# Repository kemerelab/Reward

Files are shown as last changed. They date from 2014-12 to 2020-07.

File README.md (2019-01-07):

Open Source Design for Liquid Reward in Rodent Behavioral Mazes
======

These reward wells are meant to be installed at the ends of a track. When the animal's breaks the infra-red beam at the right
location, liquid reward is delivered either via a pump or valve-controlled gravity-feed system when the animal. 

### Manufacturing
Designs are provided to 3D print the reward well. We have had success with Shapeways "White Strong and Flexible", as well as
printing in-house on our Afinia 3D printer. To prepare the food well, feed wires through the structure of the food well and
solder them to a 5 mm IR LED (e.g., [Digikey part 751-1210](https://www.digikey.com/product-detail/en/vishay-semiconductor-opto-division/TSHF5210/751-1210-ND/1681345)) and a 5 mm IR phototransistor 
(e.g., [Digikey part 475-1080](http://www.digikey.com/short/7zhpv2)). These wires are sheathed in a thick heatshrink to protect them from being eaten and then then soldered to the interface board. After testing for functionality, we expoy the LED and phototransistor into place. We additionally install a luer connection (Value Plastics [KTFLL-1](http://www.nordsonmedical.com/technical/part_drawings/KFTLL.pdf)) into the liquid feed hole at the bottom of the well.

We have ordered interface boards to be manufactured by Seeed Studio, using their PCBA service, at a cost of ~$2/unit.

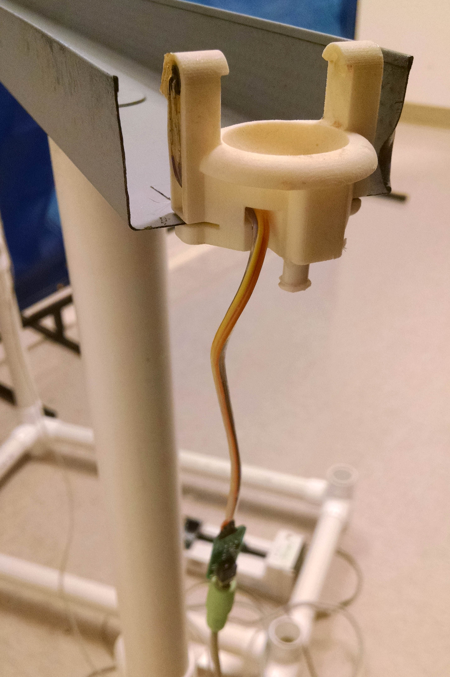
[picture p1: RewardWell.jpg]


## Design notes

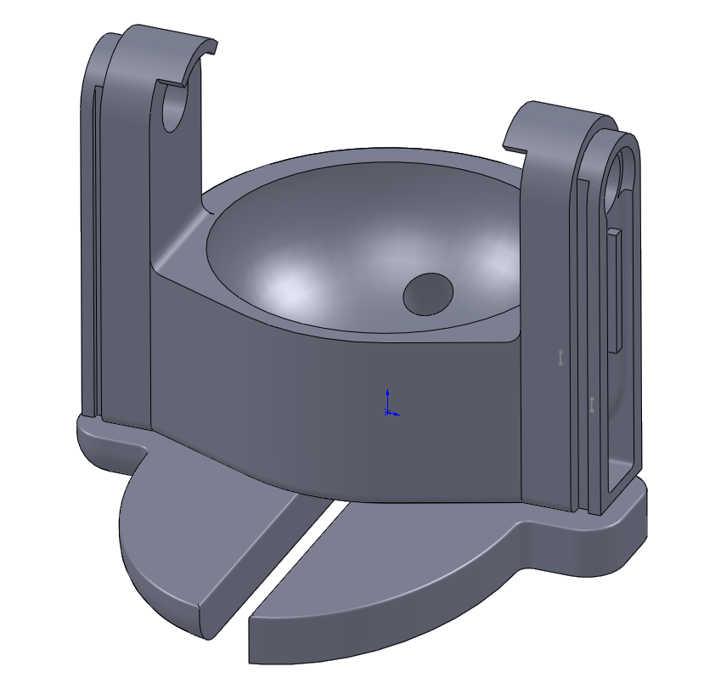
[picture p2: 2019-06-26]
OtherDesigns/RewardWellWithCaps/foodwell-all.png

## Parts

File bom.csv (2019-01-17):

Item | Purpose | Manufacturer | Manufacturer Part # | Distributor | Distributor Part # | Description | Web link
IR LED | Component for beam break system | Vishay Semiconductor | TSHF5210 | Digikey | 751-1210-ND | Emitter IR 890 nm 100 ma radial | https://www.digikey.com/product-detail/en/vishay-semiconductor-opto-division/TSHF5210/751-1210-ND/1681345
IR photodiode | Component for beam break system | Vishay Semiconductor | SFH 313FA | Digikey | 475-1080-ND | Phototransistor NPN 870 nm w/fltr | https://www.digikey.com/short/7zhpv2
Luer Connection | Interface between reward well and tubing | Value Plastics, Inc. |  | Nordson Medical | KFTLL-1 | Female Luer Thread with 1/4” Hex to 10-32 UNF Thread | https://www.nordsonmedical.com/Shop/Fluid-Management/Products/KFTLL-1
4-hole connector | Connection to syringe pump | Molex, LLC. | 3091042 | Digikey | WM1333-ND | Conn Receptacle 4Pos 0.093 | https://www.digikey.com/product-detail/en/molex-llc/0003091042/WM1333-ND/61324
Crimp pins | Pins for 4-hole connector | Molex, LLC. | 02-09-1104 | Digikey | WM1101-ND | Conn Socket 14-20 AWG Crimp Tin | https://www.digikey.com/product-detail/en/molex-llc/02-09-1104/WM1101-ND/26386
Other (don’t need specific part)
3.5 mm stereo audio cables
Arduino

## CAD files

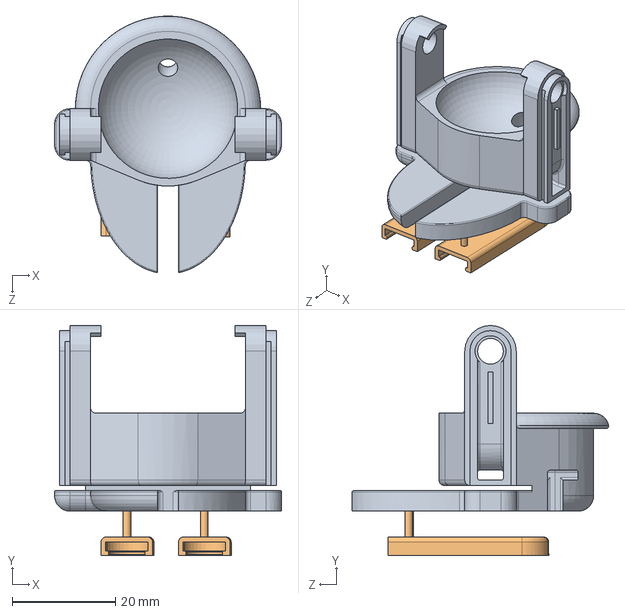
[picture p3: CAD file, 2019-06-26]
OtherDesigns/RewardWellWithCaps/foodwell-with endcaps2.SLDASM
44.0 x 44.6 x 49.7 mm
foodwell_all
foodwell_endcap x 2

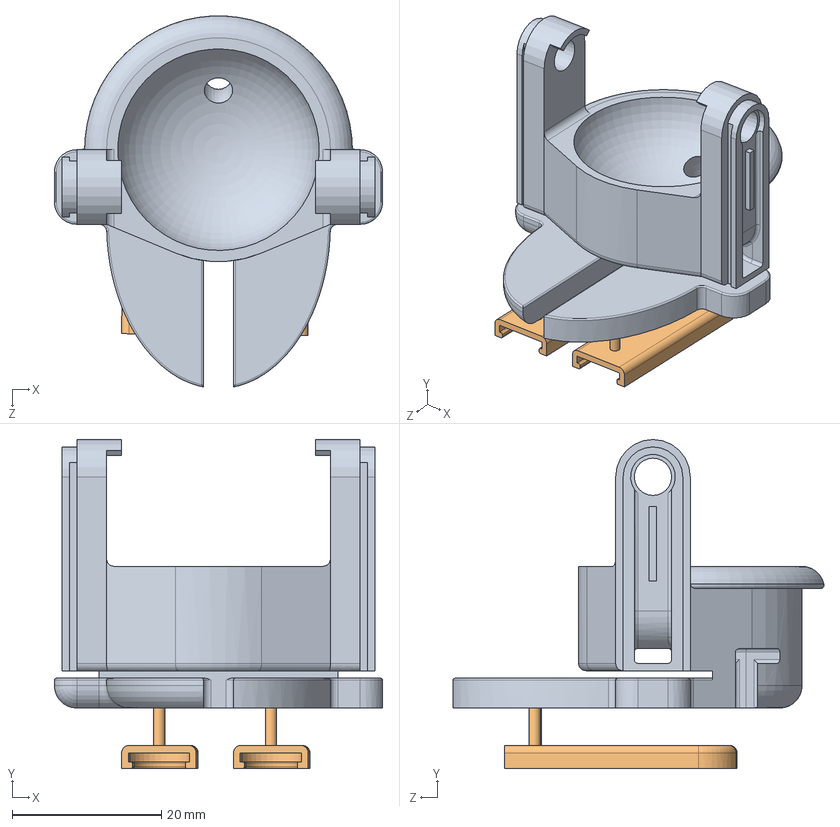
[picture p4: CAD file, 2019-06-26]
OtherDesigns/RewardWellWithCaps/foodwell-with endcaps.SLDASM
44.0 x 44.1 x 49.7 mm
foodwell_all
foodwell_endcap x 2

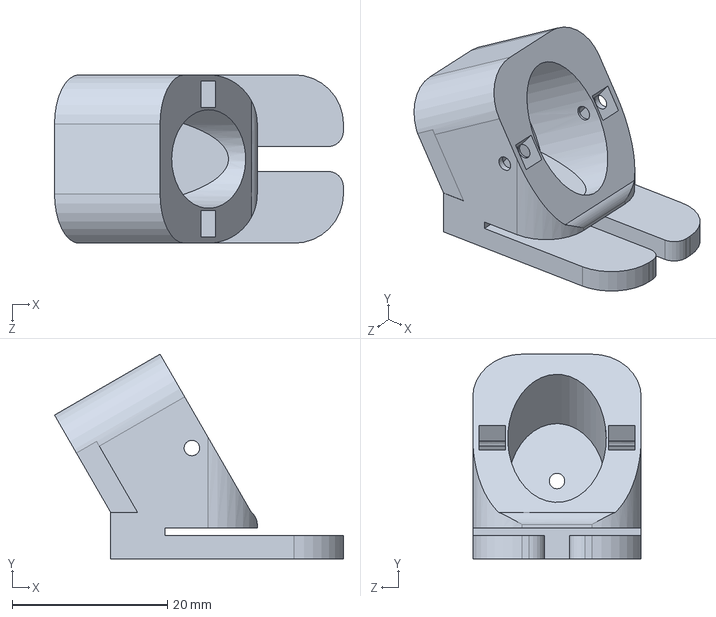
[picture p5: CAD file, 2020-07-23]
OtherDesigns/MouseWithLickSlot v5.SLDPRT
37.2 x 26.4 x 21.7 mm

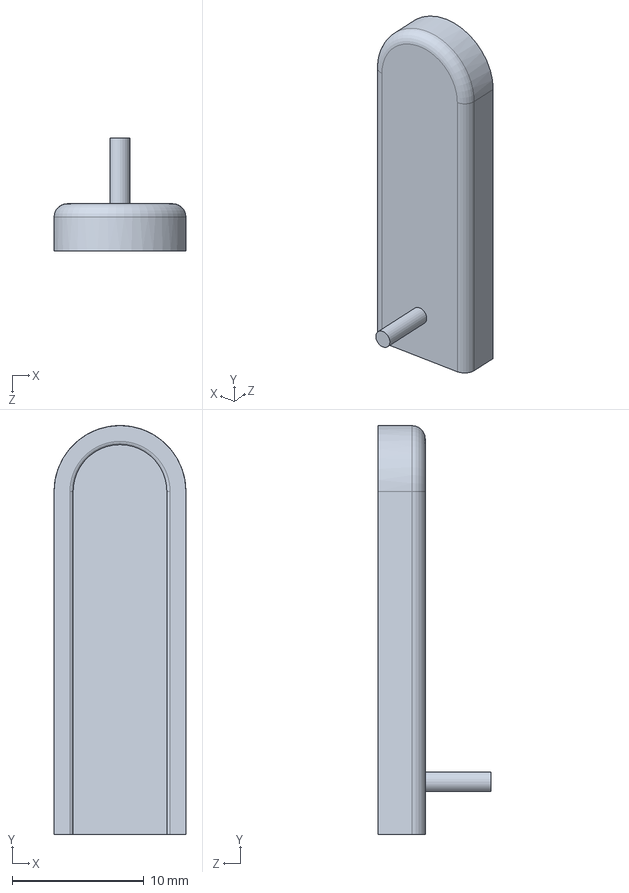
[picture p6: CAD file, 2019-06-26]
OtherDesigns/RewardWellWithCaps/foodwell_endcap.SLDPRT
10.0 x 31.0 x 8.60 mm

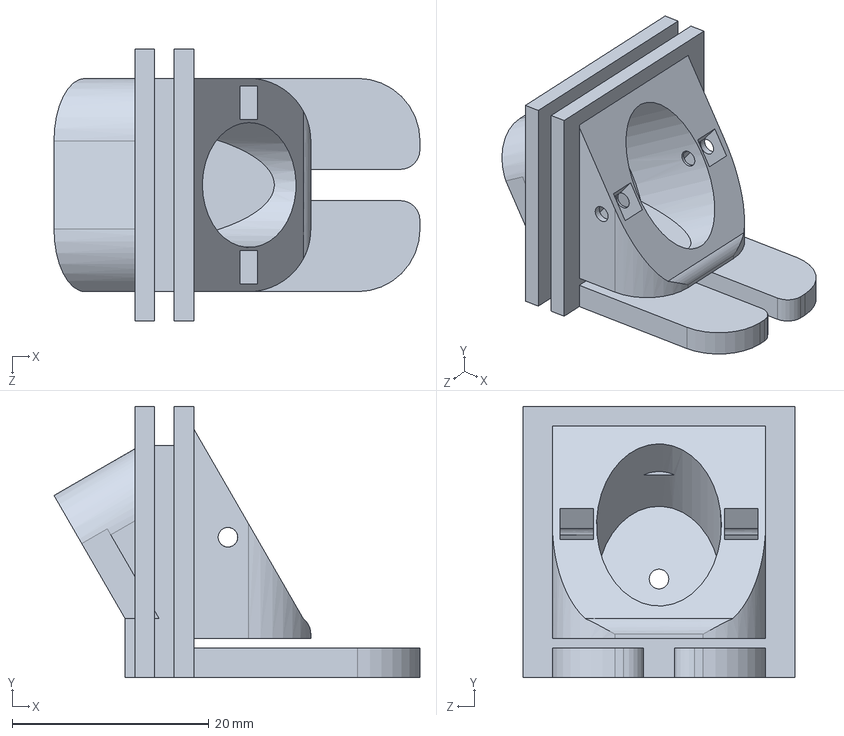
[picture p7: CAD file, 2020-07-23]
OtherDesigns/MouseWithLickSlot v6.SLDPRT
37.2 x 27.6 x 27.7 mm

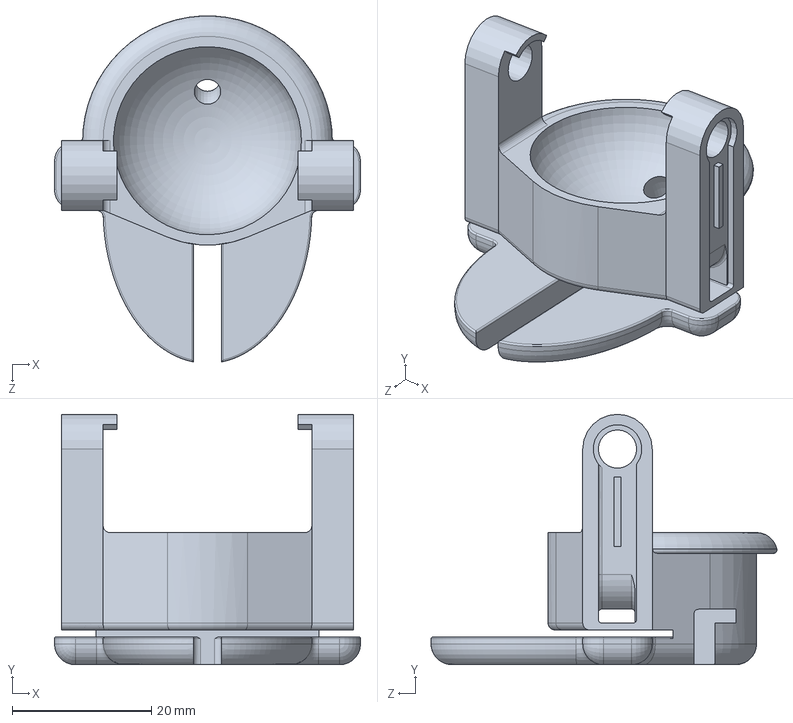
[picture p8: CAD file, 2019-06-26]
OtherDesigns/RewardWellWithCaps/foodwell_nocaps.SLDPRT
44.0 x 36.0 x 49.7 mm

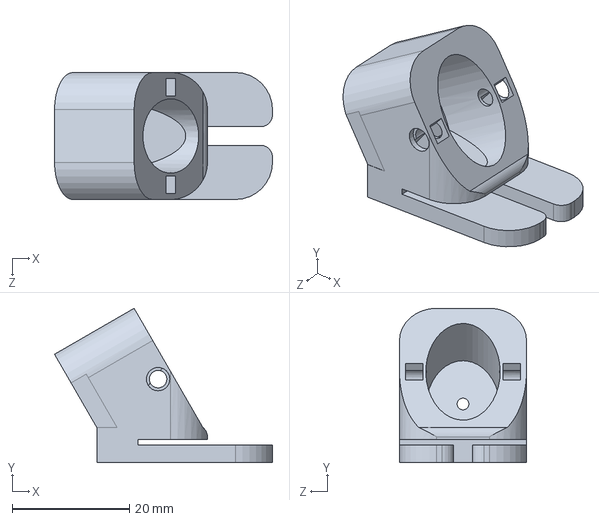
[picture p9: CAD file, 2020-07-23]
OtherDesigns/MouseWithLickSlot v3.SLDPRT
37.2 x 26.4 x 21.7 mm

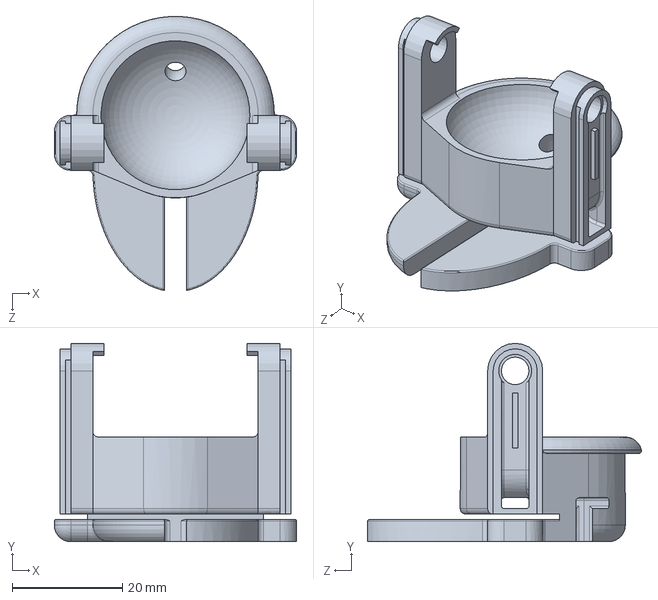
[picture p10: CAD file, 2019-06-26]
OtherDesigns/RewardWellWithCaps/foodwell_all.SLDPRT
44.0 x 36.0 x 49.7 mm

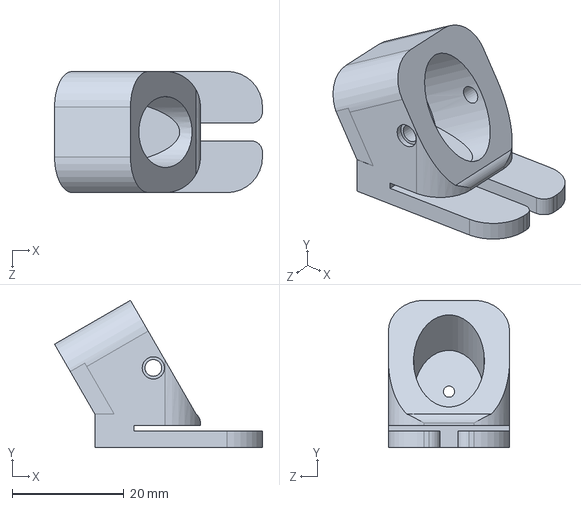
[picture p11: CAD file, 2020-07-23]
OtherDesigns/MouseWithLickSlot v2.SLDPRT
37.2 x 26.4 x 21.7 mm

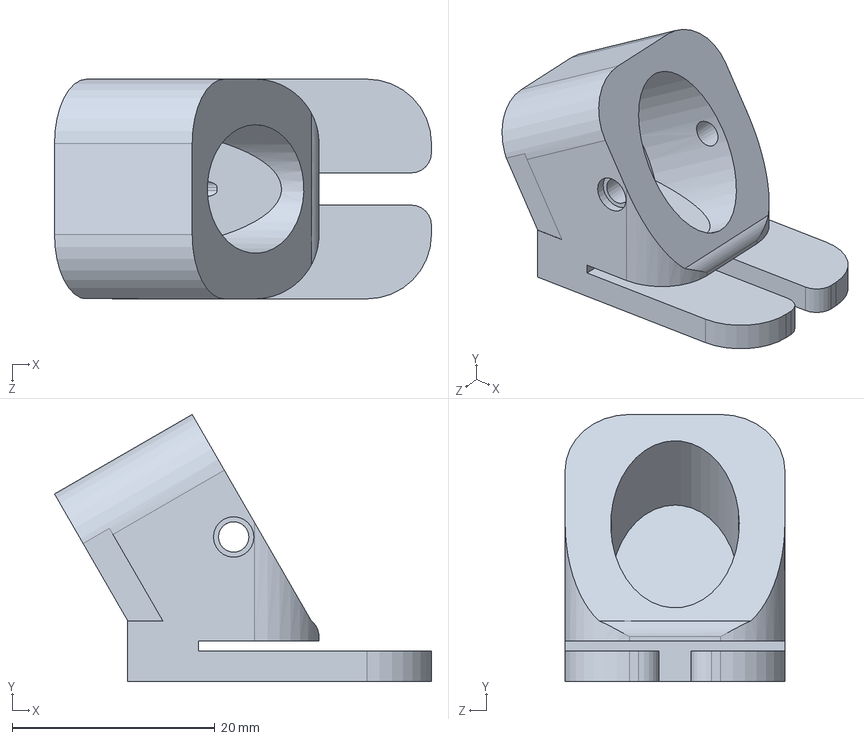
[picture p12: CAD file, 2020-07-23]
OtherDesigns/MouseWithLickSlot.SLDPRT
37.2 x 26.4 x 21.7 mm

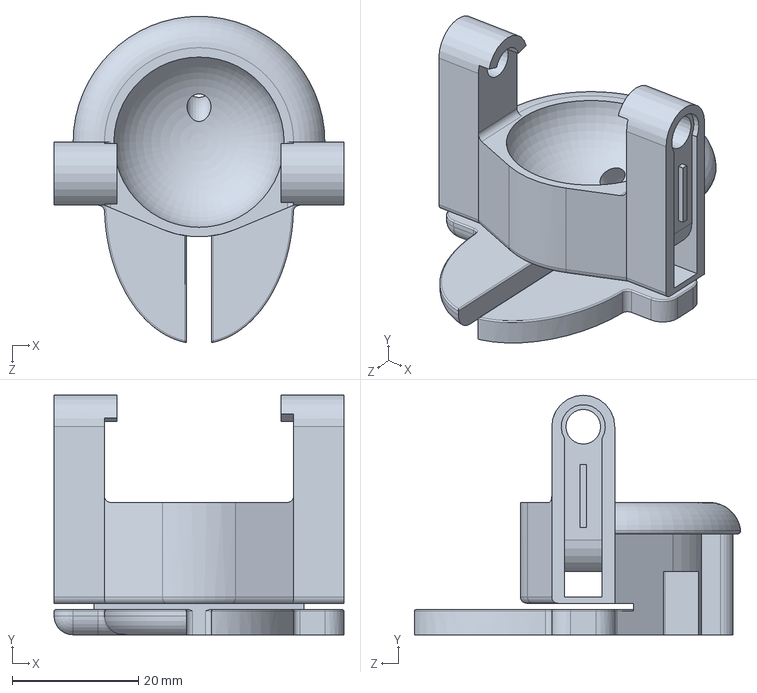
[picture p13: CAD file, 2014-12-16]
OtherDesigns/RewardWellWithCaps/foodwell_nocaps_2.SLDPRT
46.0 x 38.0 x 51.8 mm

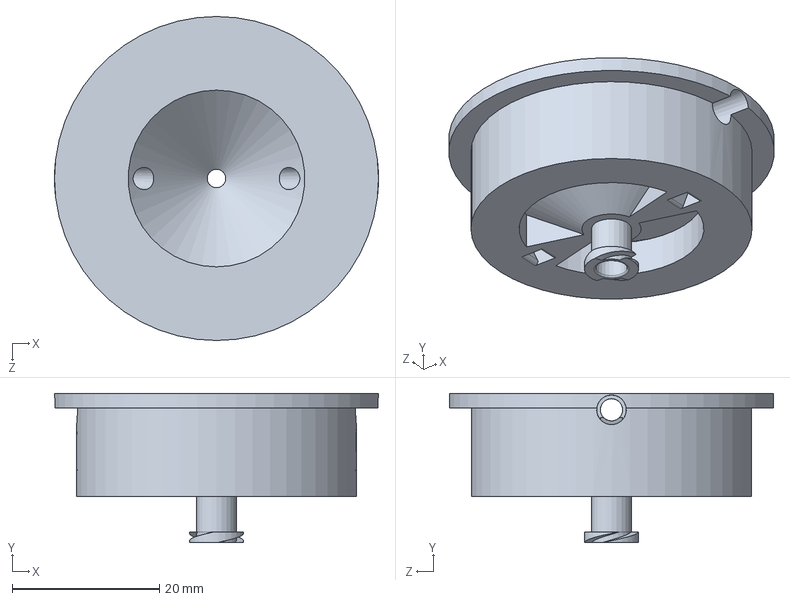
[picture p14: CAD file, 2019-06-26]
OtherDesigns/nosepoke3.SLDPRT
44.0 x 20.3 x 44.0 mm

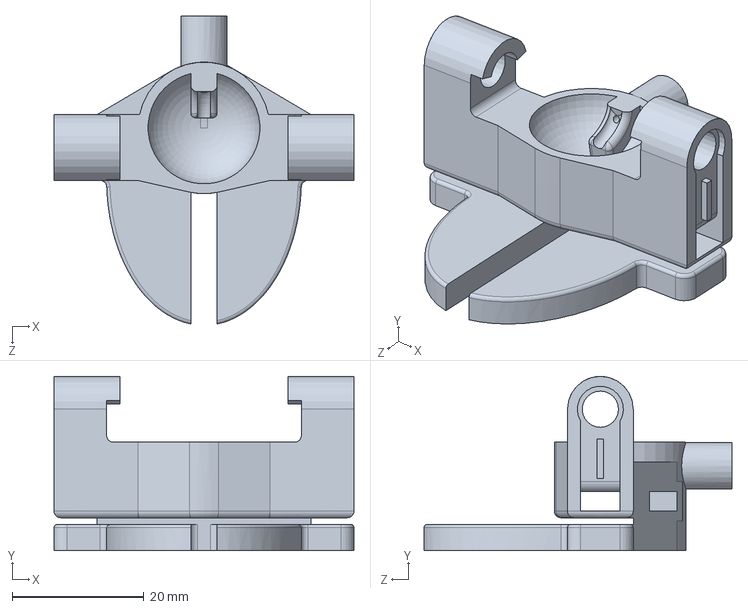
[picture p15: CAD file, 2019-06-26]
OtherDesigns/RewardWellMouse.SLDPRT
45.6 x 26.5 x 46.8 mm

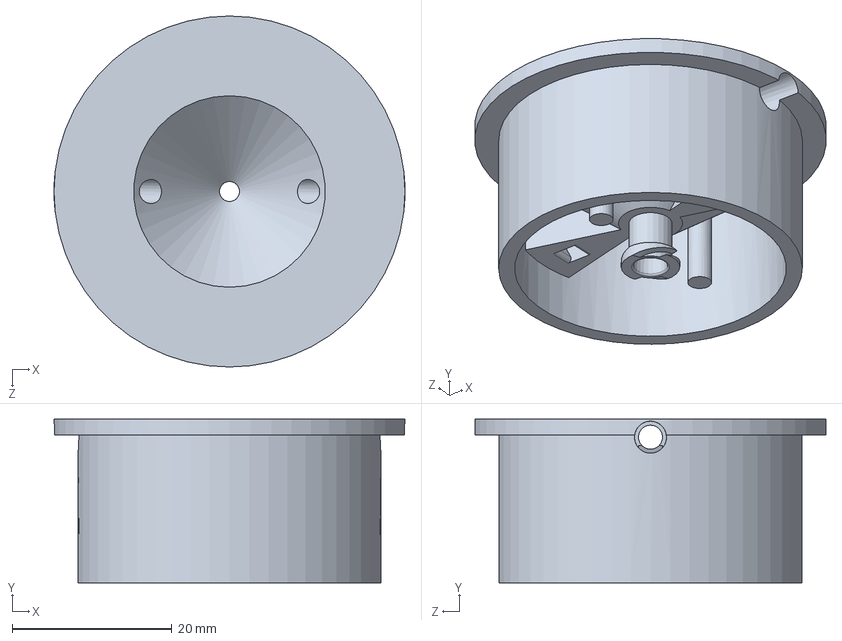
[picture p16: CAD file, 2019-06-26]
OtherDesigns/nosepoke2.SLDPRT
44.0 x 20.5 x 44.0 mm

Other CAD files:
OtherDesigns/MouseWithLickSlot v4.SLDPRT
OtherDesigns/nosepoke.SLDPRT
OtherDesigns/RewardWellMouse2.SLDPRT
OtherDesigns/nosepoke4.SLDPRT
OtherDesigns/MouseWithLickSlot v2.STL
OtherDesigns/MouseWithLickSlot v3.STL
OtherDesigns/MouseWithLickSlot v4.STL
OtherDesigns/MouseWithLickSlot v5.STL
OtherDesigns/MouseWithLickSlot v6.STL
OtherDesigns/MouseWithLickSlot.STL
OtherDesigns/RewardWellMouse3.SLDPRT
OtherDesigns/RewardWellMouse3.STL
OtherDesigns/RewardWellWithCaps/foodwell-with endcaps.STL
OtherDesigns/RewardWellWithCaps/foodwell-with endcaps2.STL
OtherDesigns/RewardWellWithCaps/foodwell_nocaps.STL
OtherDesigns/RewardWellWithCaps/foodwell_nocaps_2.STL
OtherDesigns/foodwell_top.SLDPRT
OtherDesigns/nosepoke2.STL
OtherDesigns/nosepoke3.STL
OtherDesigns/nosepoke4.STL

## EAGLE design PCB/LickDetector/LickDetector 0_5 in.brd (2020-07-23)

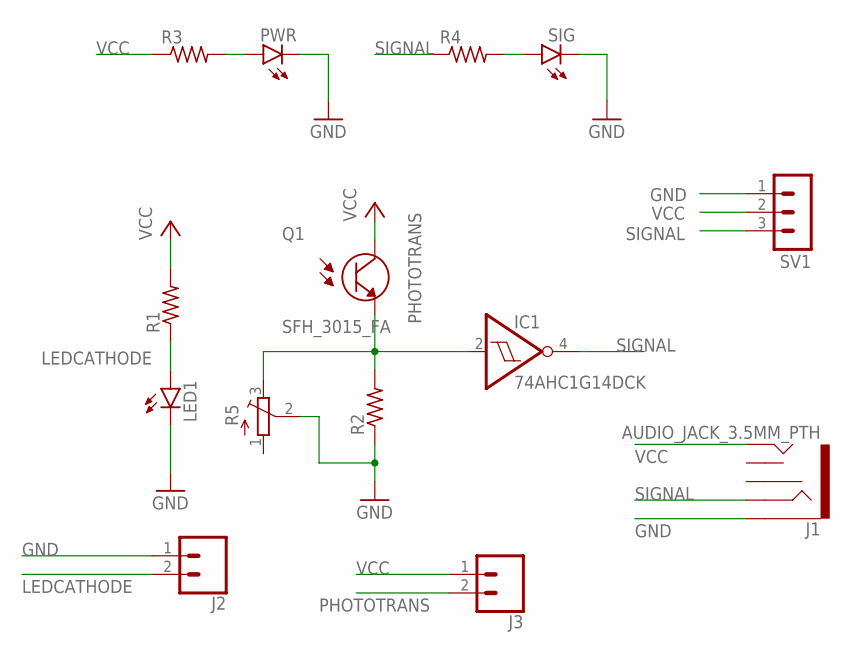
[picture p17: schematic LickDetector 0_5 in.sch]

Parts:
IC1: 74AHC1G14DCK; SC70-5
J1: AUDIO_JACK_3.5MM_PTH; AUDIO-JACK
J2, J3: CONN_02; 1X02
LED1: LEDCHIPLED_1206; CHIPLED_1206
PWR: LEDCHIP-LED0603; CHIP-LED0603
Q1: SFH_3015_FA; XDCR_SFH_3015_FA
R1, R2, R3, R4: R-US_R0603; R0603
R5: TRIM_EU-3223J; 3223J
SIG: LEDCHIP-LED0603; CHIP-LED0603
SV1: MA03-1

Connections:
GND: IC1.3 (GND), J1.SLEEVE, J2.1, LED1.C, PWR.C, R2.1, R5.2 (S), SIG.C, SV1.1
LEDCATHODE: J2.2, LED1.A, R1.1
unnamed: PWR.A, R3.2
unnamed: R4.2, SIG.A
PHOTOTRANS: IC1.2 (I), J3.2, Q1.1 (E), R2.2, R5.3 (E)
SIGNAL: IC1.4 (O), J1.RING, R4.1, SV1.3
VCC: IC1.5 (VCC), J1.TIP, J3.1, Q1.2 (C), R1.2, R3.1, SV1.2

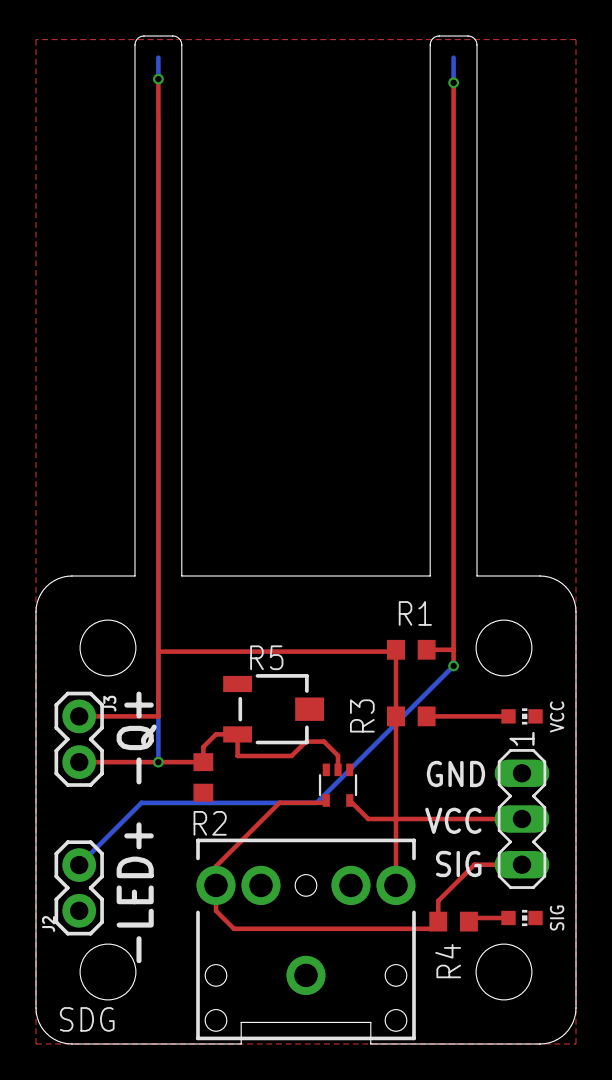
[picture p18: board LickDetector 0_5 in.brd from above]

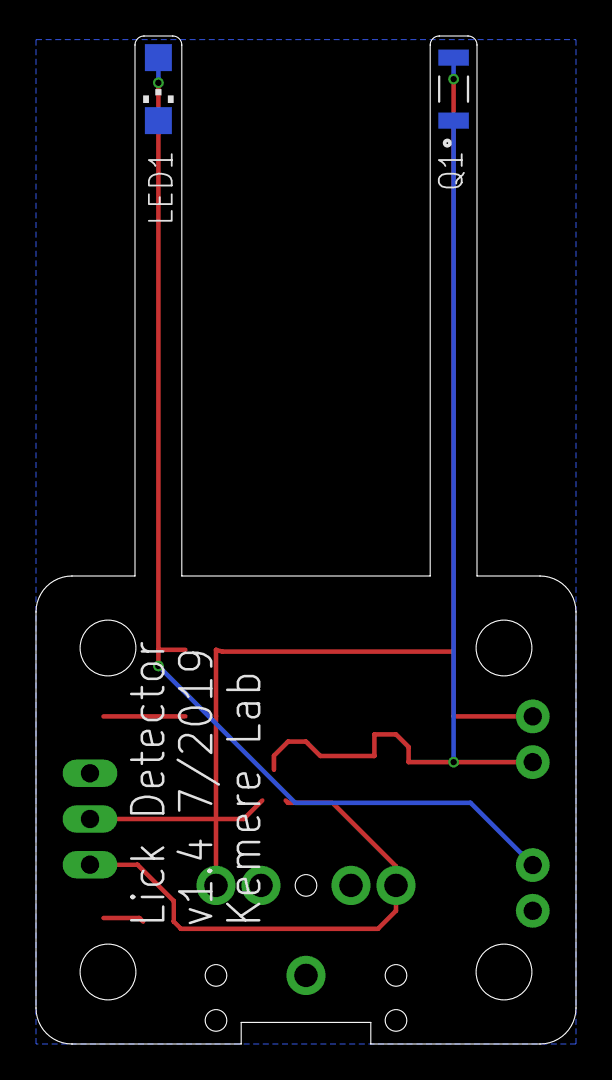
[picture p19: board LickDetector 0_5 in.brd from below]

Board: 2 copper layers, 30.0 x 56.0 mm, 14 parts (2 on the bottom side), 7 nets.

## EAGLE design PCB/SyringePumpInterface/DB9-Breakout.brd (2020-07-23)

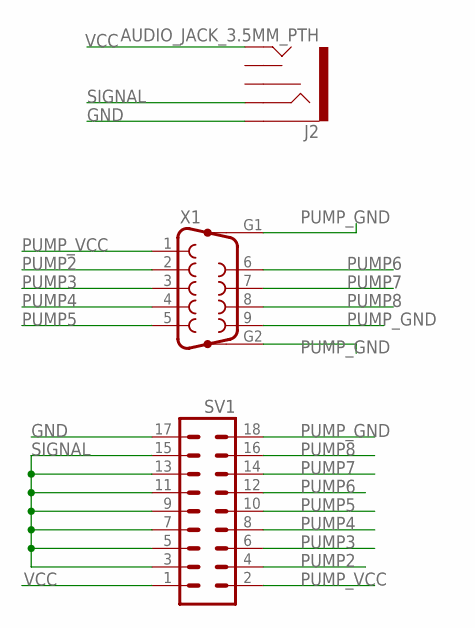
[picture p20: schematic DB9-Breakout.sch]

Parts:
J2: AUDIO_JACK_3.5MM_PTH; AUDIO-JACK
SV1: MA09-2
X1: F09HP

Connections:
GND: J2.SLEEVE, SV1.17
PUMP2: SV1.4, X1.2
PUMP3: SV1.6, X1.3
PUMP4: SV1.8, X1.4
PUMP5: SV1.10, X1.5
PUMP6: SV1.12, X1.6
PUMP7: SV1.14, X1.7
PUMP8: SV1.16, X1.8
PUMP_GND: SV1.18, X1.9, X1.G1, X1.G2
PUMP_VCC: SV1.2, X1.1
SIGNAL: J2.RING, SV1.3, SV1.5, SV1.7, SV1.9, SV1.11, SV1.13, SV1.15
VCC: J2.TIP, SV1.1

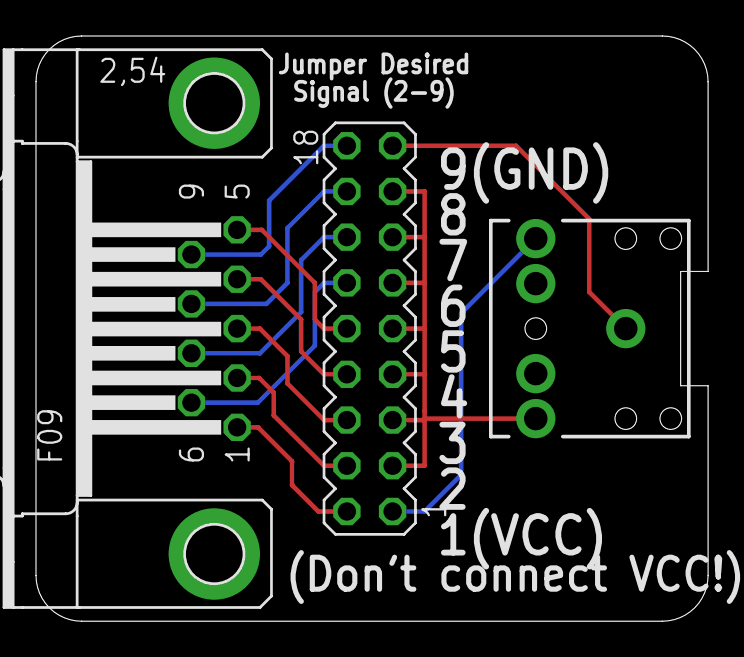
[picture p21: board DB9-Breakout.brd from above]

Board: 2 copper layers, 37.3 x 32.5 mm, 3 parts (0 on the bottom side), 12 nets.

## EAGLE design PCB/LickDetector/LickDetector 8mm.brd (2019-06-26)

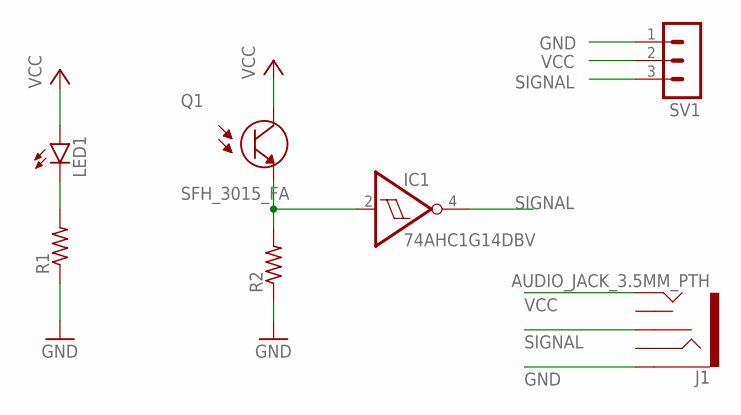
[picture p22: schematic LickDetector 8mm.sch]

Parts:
IC1: 74AHC1G14DBV; SOT23-5
J1: AUDIO_JACK_3.5MM_PTH; AUDIO-JACK
LED1: LEDCHIPLED_1206; CHIPLED_1206
Q1: SFH_3015_FA; XDCR_SFH_3015_FA
R1, R2: R-US_M1206; M1206
SV1: MA03-1

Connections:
GND: IC1.3 (GND), J1.SLEEVE, R1.1, R2.1, SV1.1
unnamed: LED1.C, R1.2
unnamed: IC1.2 (I), Q1.1 (E), R2.2
SIGNAL: IC1.4 (O), J1.RSH, SV1.3
VCC: IC1.5 (VCC), J1.TIP, LED1.A, Q1.2 (C), SV1.2

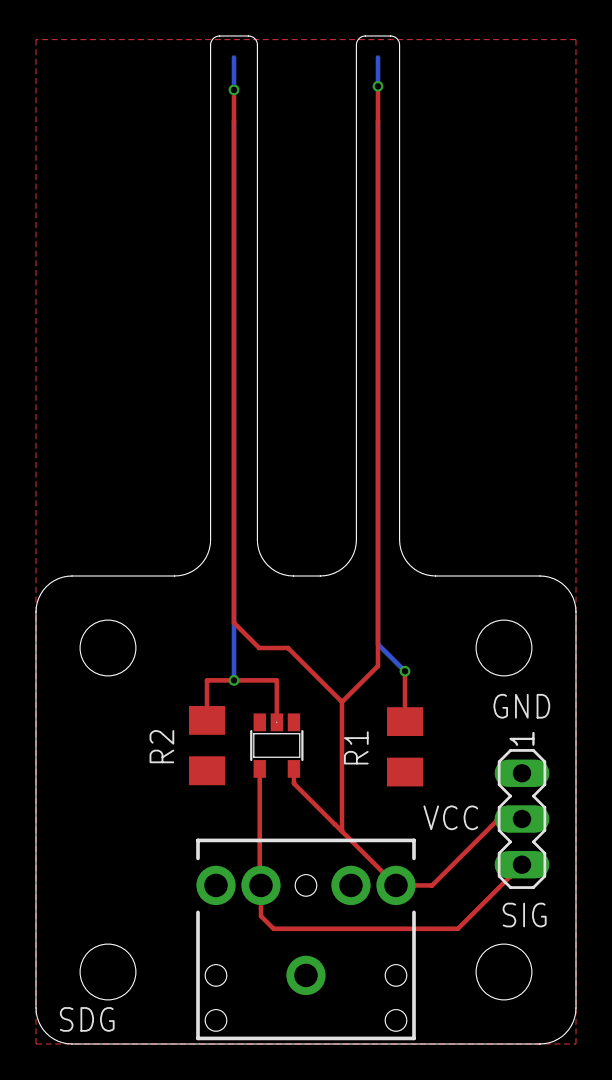
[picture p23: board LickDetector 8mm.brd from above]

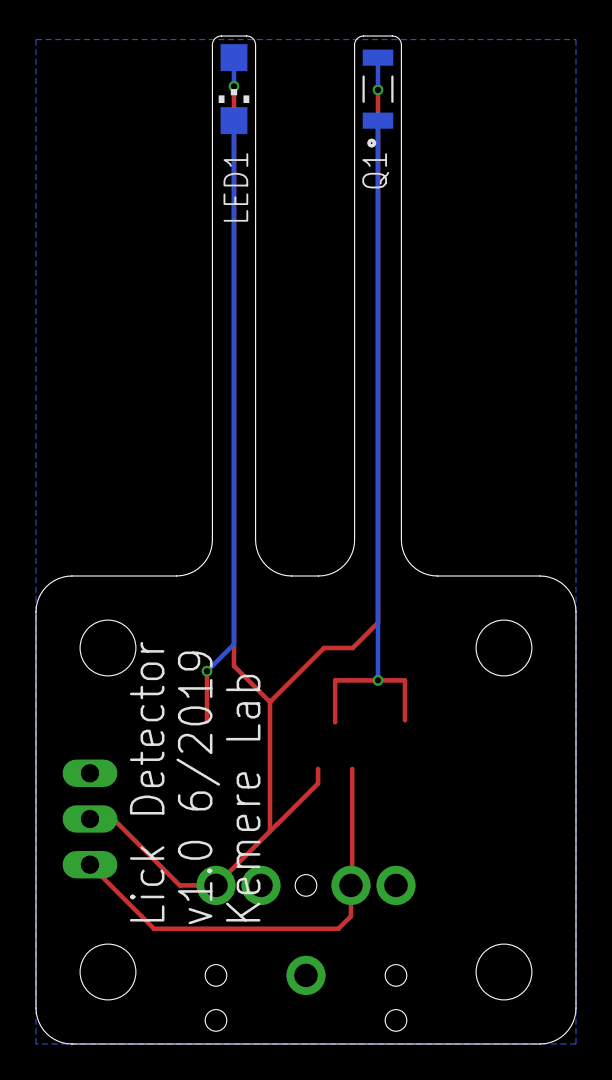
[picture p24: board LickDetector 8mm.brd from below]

Board: 2 copper layers, 30.0 x 56.0 mm, 7 parts (2 on the bottom side), 5 nets.

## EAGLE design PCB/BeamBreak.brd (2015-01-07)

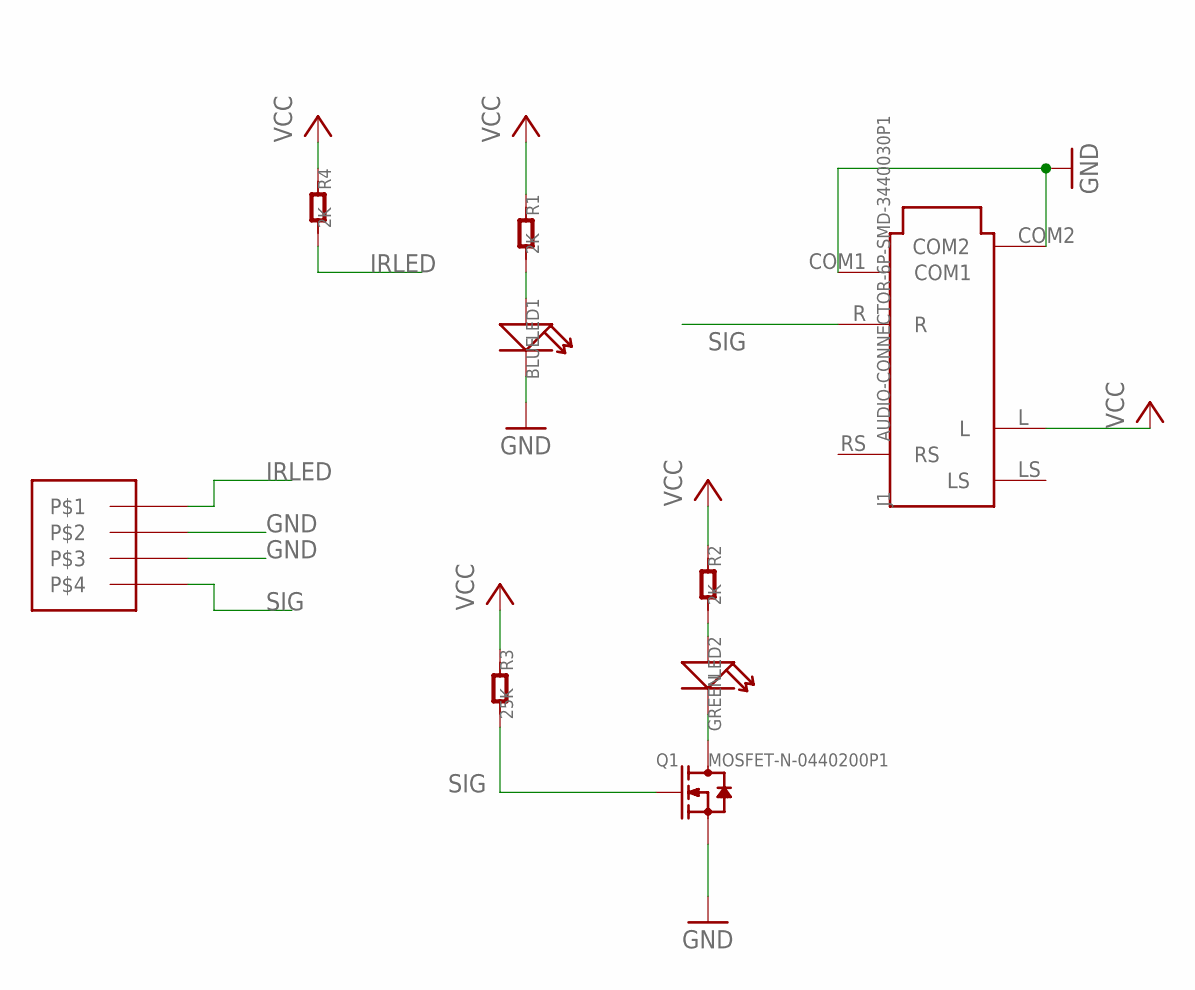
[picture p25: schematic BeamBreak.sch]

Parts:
J1: AUDIO-CONNECTOR-6P-SMD-3440030P1; 6P-SMD-3.5
LED1: BLUE; LED0603
LED2: GREEN; LED0603
Q1: MOSFET-N-0440200P1; SOT23
R1, R2, R4: 2K; R0603
R3: 25K; R0603
U$1: HO4; H04

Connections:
GND: J1.COM1, J1.COM2, LED1.-, Q1.2 (S), U$1.2, U$1.3
IRLED: R4.2, U$1.1
unnamed: LED2.+, R2.2
unnamed: LED2.-, Q1.3 (D)
unnamed: LED1.+, R1.2
SIG: J1.R, Q1.1 (G), R3.2, U$1.4
VCC: J1.L, R1.1, R2.1, R3.1, R4.1

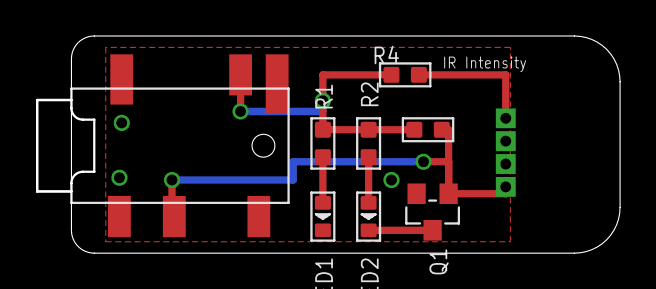
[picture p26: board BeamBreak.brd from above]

Board: 2 copper layers, 32.4 x 12.1 mm, 9 parts (0 on the bottom side), 7 nets.

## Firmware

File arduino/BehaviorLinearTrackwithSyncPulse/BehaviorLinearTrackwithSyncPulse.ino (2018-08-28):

/*
  Behavior Control with blinking LED for video synchronization
 
 General template:
 Collects input from digital inputs (e.g., beam breaks over food wells),
 and controls digital outputs (e.g., syringe pumps or valves) to provide
 reward as appropriate.
 
 This file:
 Runs the logic for a linear (i.e., back and forth) maze.
 Syringe pumps are active LOW
 
 by Caleb Kemere
 modified by Nicola Park, 2013
 modified by Etienne Ackermann, 01/21/2014 to fix bugs (startup state was previously undefined), and to add web server (subsequently removed)
 modified by Etienne Ackermann, 08/12/2016 to add LED sync
 modified by Etienne Ackermann, 09/15/2016 to change from digitalread to analogread for interfacing with SpikeGadgets ECU
 */

// Arduino input pins corresponding to food well beam breaks
const int wellA = A2;
const int wellB = A3;
const int buttonPin = 2;    // the number of the pushbutton pin

// Arduino output pins corresponding to syringe pump output controls
const int pumpA = 6;
const int pumpB = 7;
const int ledPin = 13;      // IR sync LED
const int ledMonPin = 12;   // toggled with IR sync LED, used as DIO to Trodes
const int ledRedPin = 11;   // visible LED toggled at start and end of sync, for visual feedback to user

const int dispenseLength = 500; // duration (in ms) that pump remains active per reward (1000 for 10 rpm; 500 for 20 rpm)
const long blinkInterval = 5000; // duration (in ms) between LED blinks
const long blinkLength = 30;     // duration (in ms) of LED blink

int ledState = LOW;
int syncState = true; // don't blink-n-sync until button is pressed
int buttonState;             // the current reading from the input pin
int lastButtonState = LOW;   // the previous reading from the input pin

// State information for behvaioral logic
int lastWell = 0; // during operation will alternate between 1 (=A) and 2 (=B)

// State information for output control
int dispense = -1; // signals to output service to activate a syringe pump
//  if nonzero, corresponds to output pin 
unsigned long int dispenseTime = 0; // will be the time dispensing should end
unsigned long previousMillis = 0;   // will store last time LED was updated

unsigned long lastDebounceTime = 0;  // the last time the output pin was toggled
unsigned long debounceDelay = 50;    // the debounce time; increase if the output flickers

// Reward history for webserver output
//int wellACount = 0;
//int wellBCount = 0;

void setup() {

  // initalize the input and output pins:
  pinMode(wellA, INPUT);
  pinMode(wellB, INPUT);

  pinMode(pumpA, OUTPUT);
  pinMode(pumpB, OUTPUT);

  pinMode(buttonPin, INPUT);
  pinMode(ledPin, OUTPUT);
  pinMode(ledMonPin, OUTPUT);
  pinMode(ledRedPin, OUTPUT);

  digitalWrite(pumpA, HIGH); // initially turn syringe pumps off
  digitalWrite(pumpB, HIGH); //   (they're active LOW)
  digitalWrite(ledPin, LOW); 
  digitalWrite(ledMonPin, LOW); 
  digitalWrite(ledRedPin, LOW); 

  // give the sensor and Ethernet shield time to set up:
  delay(1000);  // 1000 ms delay
}

void loop() {
  unsigned long currentMillis = millis();

  // read the state of the switch into a local variable:
  int reading = digitalRead(buttonPin);

  // check to see if you just pressed the button
  // (i.e. the input went from LOW to HIGH),  and you've waited
  // long enough since the last press to ignore any noise:

  // If the switch changed, due to noise or pressing:
  if (reading != lastButtonState) {
    // reset the debouncing timer
    lastDebounceTime = currentMillis;
  }

  if ((currentMillis - lastDebounceTime) > debounceDelay) {
    // whatever the reading is at, it's been there for longer
    // than the debounce delay, so take it as the actual current state:

    // if the button state has changed:
    if (reading != buttonState) {
      buttonState = reading;

      // only toggle the sync state if the new button state is HIGH
      if (buttonState == HIGH) {
        syncState = !syncState;
        if (syncState == true) {
          // light up red LED to indicate that syncState is not true
          digitalWrite(ledRedPin, HIGH); 
          delay(2000);
          digitalWrite(ledRedPin, LOW); 
        } else {
          // flash red LED to indicate that syncState is not true
          digitalWrite(ledRedPin, HIGH); 
          delay(500);
          digitalWrite(ledRedPin, LOW); 
          delay(500);
          digitalWrite(ledRedPin, HIGH); 
          delay(500);
          digitalWrite(ledRedPin, LOW); 
        }
      }
    }
  }

  lastButtonState = reading;

  if (currentMillis - previousMillis >= blinkInterval) {
    // save the last time you blinked the LED
    previousMillis = currentMillis;

    ledState = LOW;

    if (syncState == false){
      ledState = LOW;
    }

    // set the LED with the ledState of the variable:
    digitalWrite(ledPin, ledState);
    digitalWrite(ledMonPin, ledState);

  } else if (currentMillis - previousMillis >= (blinkInterval - blinkLength)) {
    ledState = HIGH;

    if (syncState == false){
      ledState = LOW;
    }

    // set the LED with the ledState of the variable:
    digitalWrite(ledPin, ledState);
    digitalWrite(ledMonPin, ledState);
  }
  

  // Check whether foodwells have been triggered, and reward if necessary
  if ((analogRead(wellA) > 200) && (lastWell != 1)) {
    digitalWrite(pumpB,HIGH);  // as a safety, make sure that pump B is deactivated
    digitalWrite(pumpA,LOW);
    dispenseTime = currentMillis + dispenseLength;
    //wellACount++;
    lastWell = 1;
  }
  if ((analogRead(wellB) > 200) && (lastWell != 2)) {
    digitalWrite(pumpA,HIGH);  // as a safety, make sure that pump A is deactivated
    digitalWrite(pumpB,LOW);
    dispenseTime = currentMillis + dispenseLength;
    //wellBCount++;
    lastWell = 2;
  }

  doDispense();
}

void doDispense() {
  if ((millis() > dispenseTime) && (dispenseTime != 0)) { // done dispensing
    digitalWrite(pumpA,HIGH); // (these are active low outputs)
    digitalWrite(pumpB,HIGH); // (these are active low outputs)
    dispenseTime = 0;
  }
}
 

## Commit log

2014-12-16 Initial commit. Added PCB and SolidWorks files
    [BeamBreak.brd, BeamBreak.sch, RewardWell.SLDPRT, RewardWell.STL]
2015-01-07 Changed connections for wires to a header so that solder mask will be properly applied.
    [BeamBreak.brd, BeamBreak.sch]
2018-08-28 added linear track arduino controller code
2018-08-28 added w maze arduino controller code
2019-01-17 Added BOM for easier tracking of parts
    [bom.csv]
2019-06-25 Added a bunch more designs
    [RewardWellMouse.SLDPRT, RewardWellMouse2.SLDPRT, RewardWellMouse3.SLDPRT, RewardWellMouse3.STL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]
2019-06-26 Added long-narrow beam break PCBs in different sizes.
    [LickDetector 0_5 in.brd, LickDetector 0_5 in.sch, LickDetector 8mm.brd, LickDetector 8mm.sch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]
2019-06-26 Added side-view LED datasheet for lick detector PCB.
2019-07-10 Added power and signal LEDs to Lick Detector beam break PCB
    [LickDetector 0_5 in.brd, LickDetector 0_5 in.sch]
2019-07-10 Added DB9 syringe pump board with jumper header for flexibility
    [DB9-Breakout.brd, DB9-Breakout.sch]
2020-03-11 Fixed bug where wrong audio jack pin was connected for signal. Also added cuttout for jack and potentiometer
    [LickDetector 0_5 in.brd, LickDetector 0_5 in.sch]
2020-07-23 New mouse-scale nose poke foodwell designs added. Also a flexible PCB beam break pcb. Also updated DB9 breakout for the syringe pump that has a jumper to choose the pulse pin.
    [DB9-Breakout.brd, DB9-Breakout.sch, LickDetector Flex.brd, LickDetector Flex.sch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]

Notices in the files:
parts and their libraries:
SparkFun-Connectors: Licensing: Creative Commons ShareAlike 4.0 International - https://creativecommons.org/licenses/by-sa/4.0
